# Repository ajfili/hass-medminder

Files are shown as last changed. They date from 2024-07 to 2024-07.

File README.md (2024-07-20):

# hass-medminder
A Home Assistant / ESPHome based medication reminder for tracking and reminding about medications and refills

As a person who is not particularly functional when I first wake up, as well as having ADHD, I have trouble remembering to take medications first thing in the morning. I've used the medication reminder built into iOS Health for a while with moderate success, but the number of times my phone reminds me to take it and then I have to count pills in my "initially conscious" state to see if I took it immediately when I woke up a few minutes prior is far too high. I'm a Home Automation nerd and figured leveraging HASS and ESPHome to solve a problem while making my first self-designed ESPHome project to develop my skillsets was a good use of my time.

I built a janky prototype out of a drilled 3d printed box and lots of dupont connectors and hot glue. But it didn't work half bad.

As I thought about what I wanted to improve and discussed it with a few people on some HASS discussion pages, I realized this might have some use for people who also have a hard time remembering to take their medication, or even a family tracking if someone already gave the dog/cat their medication today, etc. I wanted to release it out there so other people could benefit from what I built. So I went back to the drawing board and redesigned the whole project. Instead of using 8-10 HASS helper entities, I leveraged the Event bus more. I took logic out of the ESP and moved it to HASS and vice versa. If I was going to release it to the world, I wanted to at least release something better than v1

This is my second iteration, and while better than the first version, I'm sure this can definitely be cleaned up a bit. I apologize for any janky code, or the poor design of the casing. I merely was inspired by a design in Thingiverse and slapped some modifications onto it in TinkerCAD for a quick and dirty enclosure I could make ASAP. One of the things on my to-do list is to sit down and work on my CAD skills so I can design an enclosure from scratch, but if anyone wants to take a crack at it, I would love if you shared it with me. Any constructive feedback towards this project is welcomed, as it can only help me get better at this stuff.

In this repo are the following:

* **medminder-esp.yaml** - This file is my esphome yaml config for the D1 Mini. I have redacted the OTA and API keys, so you will have to manually enter them or simply copy and paste everything from line 30 and below into a preinstalled ESPHome config for your board
* **medminder.yaml** - This is the Home Assistant automation I'm using to drive this. It requires 5 helper entities to be created to maintain the state of things. Please see my write up below for the names I used, and if you want to change them, please change their references in the ESPHome config and in the automation as well so it can work for you.
* **MedMinder-Top.stl** - The top casing, where everything gets mounted to. It's not my finest work, but it printed perfectly fine in PLA+. I printed it in the orientation provided (bottle holder pointing up) and just did snug supports for the inner ceiling. Took about 2-3 hours on my Prusa Mk4 in PLA+
* **MedMinder-Bottom.stl** - A snapfit bottom but the tolerances might not be great. I used a few dots of hot glue to increase the friction between the pieces for now. 

# Goals

I had a few goals I wanted to accomplish with this project:

* Simple to use for regular people. Not everyone in the household can build or implement this, but placing a bottle in the holder or pushing the single button is pretty straight forward.
* Inexpensive
* Maintain most of the state/important data in HASS. The ESP is merely an input/output based on what is in Home Assistant. I know a lot of this code can be done entirely within the ESP, but I decided not to for reliability of maintaining the info during power outages and whatnot. My Home Assistant lives on a NUC in a server rack powered by a UPS. The ESP is plugged into a USB port on my nightstand, I didn't want to trust important data there.

# Requirements:

## Hardware BOM:

| Part | Qty | Link | Notes |
| --- | --- | --- | --- |
| WEMOS D1 Mini (ESP8266) | 1 | <https://a.co/d/5cXB2x8> | Went with the D1 Mini as I found an enclosure for this and the chosen PN532 module already, but you can use any ESP device. It just may require more modification to the ESPHome config. |
| PN532 RFID/NFC module (HW-147 red type) | 1 | <https://a.co/d/5j30uwH> | There are many out there, including the probably "easier to build around" Adafruit model. Again, found an enclosure that fit this one so that's what I went with. |
| 3mm Red LED | 1 |  |  |
| 3mm Green LED | 1 |  |  |
| 3mm Blue LED | 1 |  |  |
| 440Ω Resistors | 3 |  |  |
| Momentary Switch | 1 | <https://a.co/d/dofvmd4> | Any SPST Normally Open button will work here. The hole in the STL I used for the casing can take any 12mm button, but be careful on the depth. Anything deeper than \~13-15mm will be too big for the case. The button I used has an integrated LED as well, that I may integrate as a status LED or something. For an example without the LED see here: <https://a.co/d/6wV9Lmx> |
| NFC sticker | N/A | <https://a.co/d/ftuGgJh> | Any adhesive NFC sticker should work, they're cheap, and a 40 pack like this should last you over 3 years, assuming a 30 day supply each time. |

## Wiring Map:

This wiring map is only for use with a ESP8266 based Wemos D1 Mini. The number of connections will be the same, but GPIO pin mapping may vary if you use a different board.

| Physically Labeled Pin | GPIO Pin in ESPHome | Color Wire to Use | Connecting |
| --- | --- | --- | --- |
| 3v3 | N/A | Red | PN532 VCC |
| D1 | GPIO5 | Green | PN532 SCL |
| D2 | GPIO4 | Yellow | PN532 SDA |
| D4 | GPIO2 | White | Button NO terminal |
| D5 | GPIO14 | Red | RED LED + |
| D6 | GPIO12 | Green | Green LED + |
| D7 | GPIO13 | Blue | Blue LED + |
| D8 (Optional) | GPIO15 (Optional) | Blue | Button + Terminal |
| G | N/A | Black | PN532 G, - terminal of all three LEDs, - terminal of button, NO terminal on button |

## Home Assistant Helper Entities:

I've included the list of entities and what I named them below, if you want to use different ones, that's fine, but you will need to change the entity names in the ESPHome config as well as the Home Assistant automation script.

| Entity Type | Entity Name | What it does |
| --- | --- | --- |
| Dropdown | input_select.medminder_status | This is a dropdown that is the current status of the system, which can be one of four states: "Armed", "Disarmed", "Taken" and "Skipped". A full explanation of them is below. |
| Text | input_text.current_bottle_tag | This is populated by the ESP whenever you place a tagged bottle on the reader. It's mainly for comparing yesterday's tag to todays and if they change, then a 30 day cycle starts again |
| Text | input_text.last_bottle_tag | This is used to compare against the currently read tag from ESP. If they're the same, then the pill count is decremented and the status switches to taken (if status is armed). If the tags differ, then a new 30 day cycle begins, with a reminder created. |
| Number | input_number.pills_remaining | This is merely a count of the remaining pills in the 30 day cycle and has no other functionality in the app. Could be discarded if you don't need it. |
| Toggle | input_boolean.medminder_sleep_mode | This controls the sleep mode state. Sleep mode turns off the LEDs so if you have it on a nightstand the lights don't disturb you. This does not change the status of the system itself, just if the lights are on or off. Scheduling this is a possibility. |
| Local Calendar | calendar.medication_reminder | When a new tag is read, a calendar event is created 24 days from now at 10am. When the current time hits that event, a notification is triggered. |

## Explanation of operation

There are two main states we track in the system:

**Medminder Status** - This is the main control mechanism for MedMinder, and the three LEDs on the front indicate the status.

* Armed - Red LED on

  In the armed state, three things can happen.

  1- A tag is read, which means the medication was taken. MedMinder Status is set to "Taken"

  2- The button is pressed, which means the medication was skipped for the day. Status is set to "Skipped"

  3- The button is long pressed, which sets the system to "Disarmed".
* Taken - Green LED on

  Indicates the med was taken, and will stay in this state until the set time of day to "rearm" occurs
* Skipped - Blue LED on

  Indicates the med was skipped for the day, and will stay in this state until the set time of day to "rearm" occurs
* Disarmed - All LEDs off

  The system is turned off. This is useful if you need to mess with the tag or swap bottles without triggering the reset of the cycle.

**Sleep Mode** - This can turn off the LEDs without affecting the status of the system. Ideal for those who keep their AM medication on a nightstand next to their bed, by reducing light pollution in your bedroom . If the MedMinder will live somewhere else where the lights wont disturb sleep, you can ignore this and rip it out of the code if needed.

## Automation Flow Explanation:

8 events trigger the automation:

1. When a tagged bottle is placed on the reader

2. When the button is single pressed

3. When the button is long pressed

4. When the scheduled rearm time occurs

5. When the scheduled sleep mode start time occurs

6. When the scheduled sleep mode stop time occurs (currently sunrise)

7. When the time to request a refill occurs (Based off event in dedicated calendar entity)

8. When a time of day is reached but the system still shows as "armed"

Triggers 4, 5, 6 and 8 are all coded into the automation triggers and can be modified to fit your desired use case

The above triggers correspond to the following logics:

1. When bottle is placed on the reader, if the tag changes, the previous tag is updated to the new one, the pill count is reset to 30, and a calendar event is created 24 days in the future (at 10AM). Then if the system is armed, the status is changed to "Taken", and the pill count is decreased by 1.
2. When the button is pressed, and the system is armed, the status is set to Skipped.
3. If the button is long pressed, it will toggle the status between "Armed" and "Disarmed"
4. When the set time of day occurs, the status is set to "Armed"
5. When the set time of day occurs, sleep mode is turned on, which will turn off the main status lights, and turn on the LED in the button
6. When the set time of day occurs, sleep mode is turned off, which will turn the status lights back on based on the current status, and turn off the button LED.
7. When the current time is within the time for the created (25 days after the last bottle tag change) calendar event, a notification is fired off
8. When the set time of day occurs, it checks if the system is still armed and if it is, will fire a notification to remind to take it.

## Current plans for the future reversions

* Would like to consolidate the three LEDs down to one RGB LED or perhaps a NeoPixel ring around the holder. I think this would simplify wiring and make it look a bit nicer.
* Instead of having such a deep cavity for the container, perhaps a recess or something more open. Easier to print, can handle different/larger bottles, and would look nicer.
* Perhaps an i2c multiplexer and the ability to track multiple medications.
* Actionable HASS notifications, allowing to skip or logged as taken from the reminder notification in case it doesn't trigger for some reason

### Attribution:

A big thanks to MrGreen90 for his work on the case that I used for the basis of the one I used in this build. His original model can be located here: <https://www.thingiverse.com/thing:3609603>

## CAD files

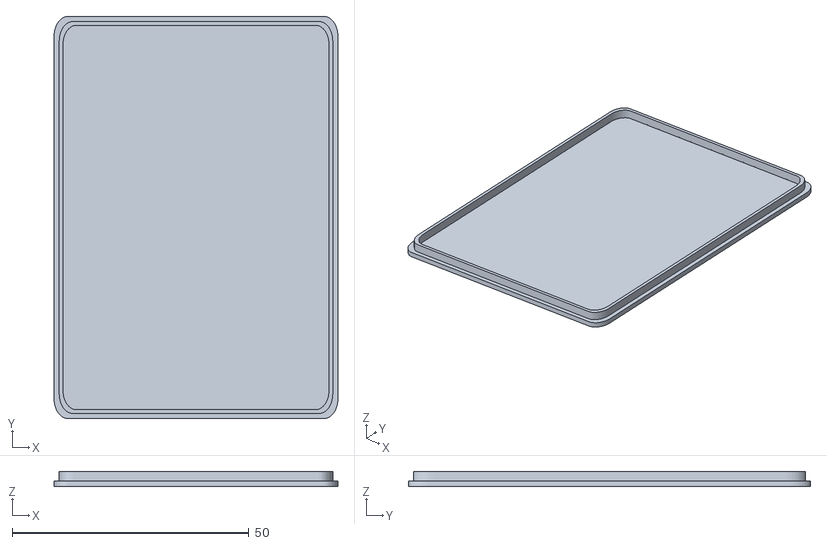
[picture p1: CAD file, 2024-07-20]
MedMinder-Bottom.stl
60.0 x 85.0 x 3.20

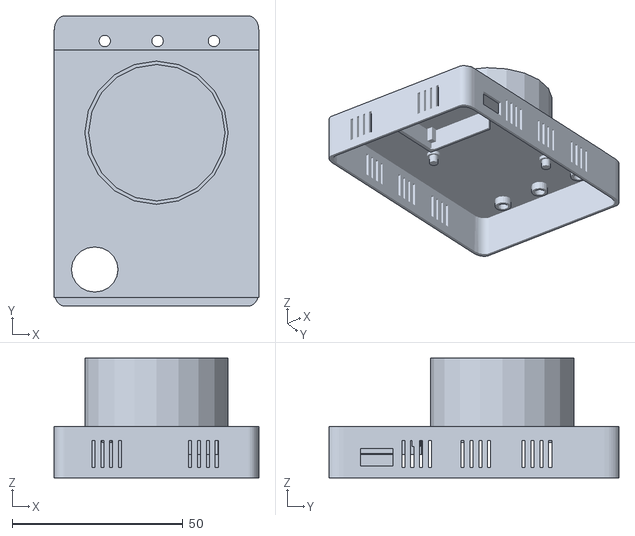
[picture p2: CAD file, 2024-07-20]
MedMinder-Top.stl
60.0 x 85.0 x 35.1
